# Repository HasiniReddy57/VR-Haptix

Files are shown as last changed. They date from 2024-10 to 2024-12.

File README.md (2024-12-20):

# Haptic Feedback for Stroke Rehabilitation in Virtual Environment
This is a repository to track the progress of our capstone project 'Spinoverse, Haptic Feedback System for enhanced Virtual Reality experience'

# Unity Project Setup Guide

Access the Unity project and follow the setup instructions using the link below:

- **Unity Project Repository**: [VR-Haptix-Environment](https://github.com/HasiniReddy57/VR-Haptix-Environment)

This repository contains the complete Unity project files and a comprehensive setup guide in the README file.

---

### Standalone Unity Environment Setup

The project is designed for standalone environments, ensuring it runs independently with minimal external dependencies. Please refer to the repository's README for detailed instructions.

---

### Credits

VR Environment developed and maintained by [Hasini Patlolla](mailto:hpatloll@uci.edu).

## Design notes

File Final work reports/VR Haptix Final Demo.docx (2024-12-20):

Haptic feedback for stroke rehabilitation in virtual environment

Final Prototype Link:

https://www.youtube.com/watch?v=wLWnkHBS-OE

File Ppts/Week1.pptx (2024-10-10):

## Team Haptix 2.0 Capstone Project Update

## Application Update

Haptix for Physiotherapy/Pain relief
Existing Application
TENS - https://uihc.org/health-topics/transcutaneous-electrical-nerve-stimulator-tens

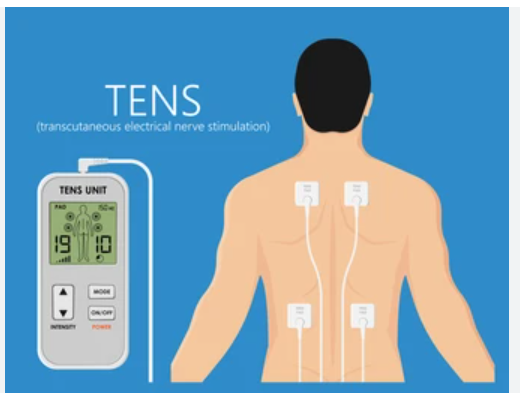
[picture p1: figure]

## System Design

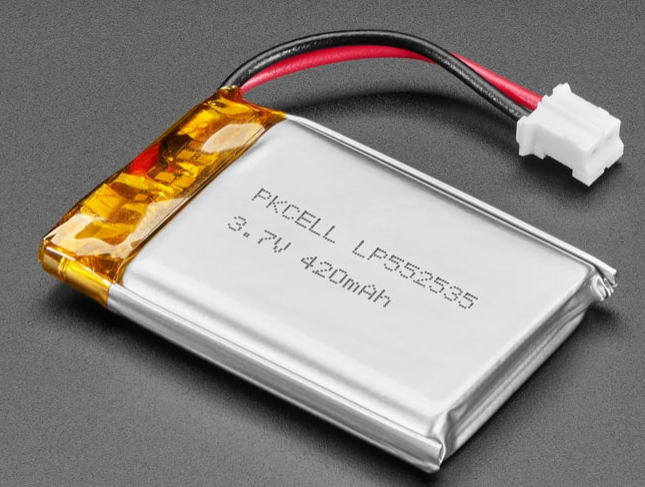
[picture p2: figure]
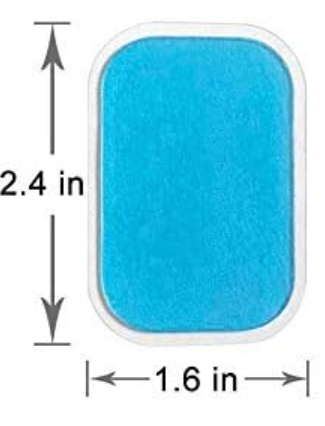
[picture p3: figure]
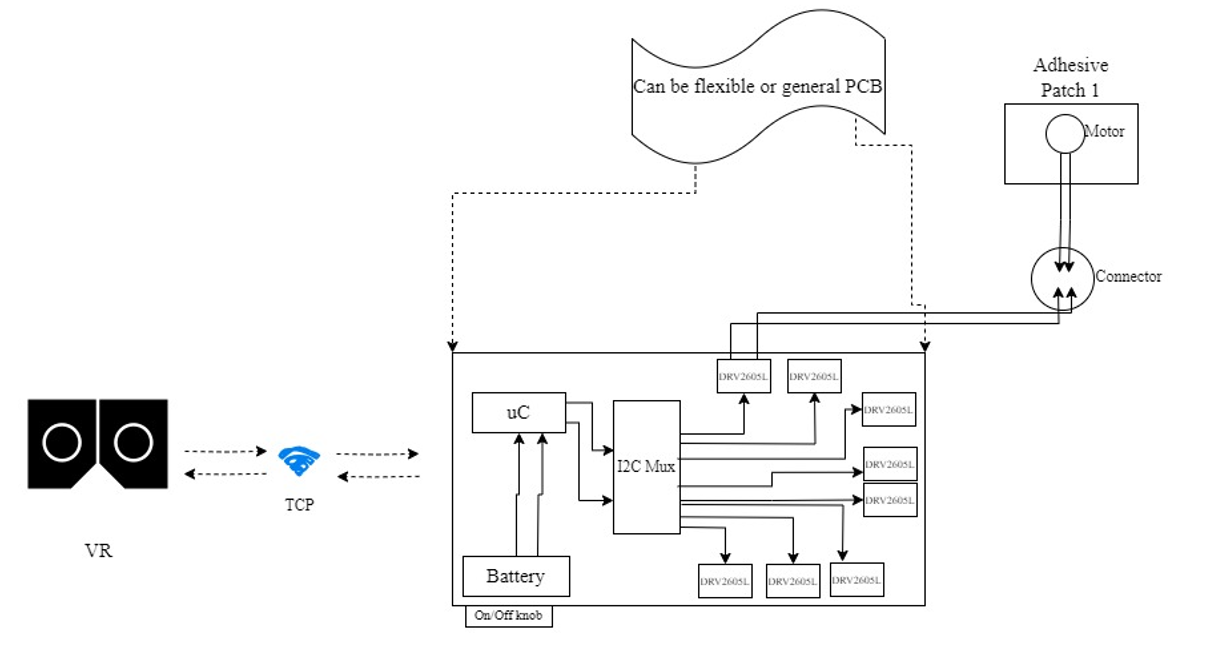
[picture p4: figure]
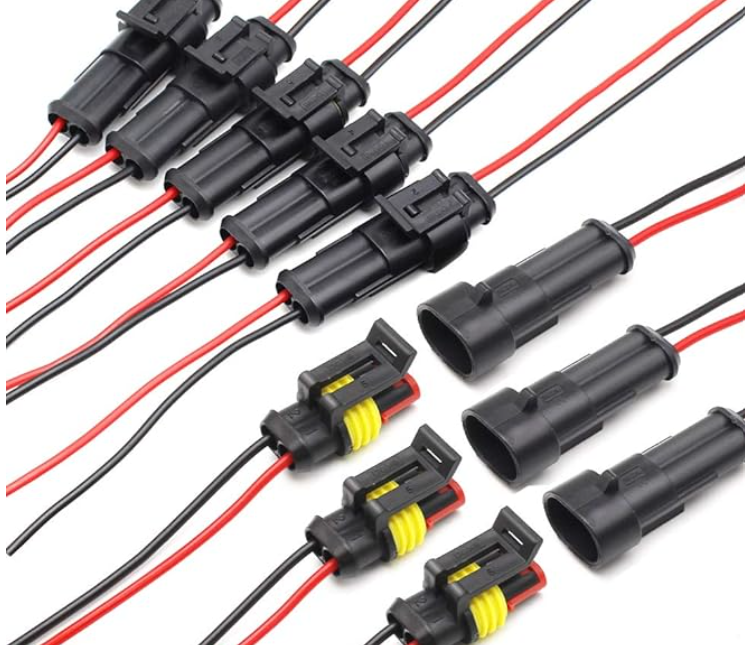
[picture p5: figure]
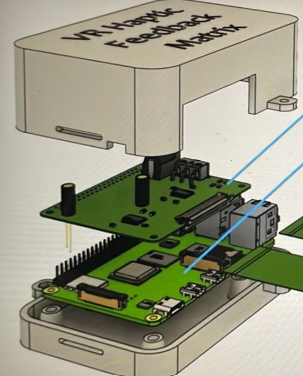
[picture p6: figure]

## Components & Communication

Components
1. DRV2605L
2. Actuator – Tested ERM
3. I2C mux – TCA9548A
4. Controller – ESP32
5. Battery - LiPo
6. Power knob
7. Adhesive patch
8. Connectors
9. VR
Communication
1. I2C
2. TCP

## Voltage, Current, Power requirements

- ERM motor:
- Voltage supply – 2 to 5v
- Current drawn by the motor – 40-80mAmp
- Power – 80-400mW
- ESP32
- Voltage supply – 2 to 5v
- Current drawn by the ESP32 – 80-130mA (without Wifi)
Start up no WiFi 40-45mA, Flash Mode 20-25mA, With WiFi 120-125mA
- Power - 481mW (with Wifi)
- DRV2605L
- Voltage supply – 2 to 5.2v
- Current drawn by the DRV2605L – 10mA to 30mA
- Power - 2.2mW

## Contd…

- TCA9548A
- Voltage supply –1.65V to 5.5V
- Current drawn by the motor – 3μA (inactive) to 600μA (active)
- Power - 15μW to 3mW

## Motor types – ERM, LRA, FEA

## PCB designing

- Followed tutorials on schematic and PCB layout. Need support with routing and further steps.

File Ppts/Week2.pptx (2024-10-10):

## Team Haptix 2.0 Capstone Project Update

## Driver updates

- DRV8833
- DRV2603
- But not for Haptic applications. Supports servo motors.
- DRV2605 & DRV2605L – Haptic drivers with ERM motors

## Power calculations

Tested with 3.3v, 170mAh battery.
Initial battery - 3.869v (actually 4.2v according to datasheet)

- Same Battery connected to ESP32 and other circuit
- Battery voltage – 3.7v
- Run time – 1hr
- When voltage drops to 3.57v, ESP32 went to sleep mode.
- Entire circuit draws 0.169Amps ~ 170mA
- Separate Battery connected to ESP32 and Other circuit
- Battery voltage – 3.81v
- Run time – 1hr 20 mins
- The circuit was working till 3.3v battery but below 3.5v, some On-board LEDs of driver are fluctuating. Not sure if its because of loose connections on bread board.

## PCB Layout

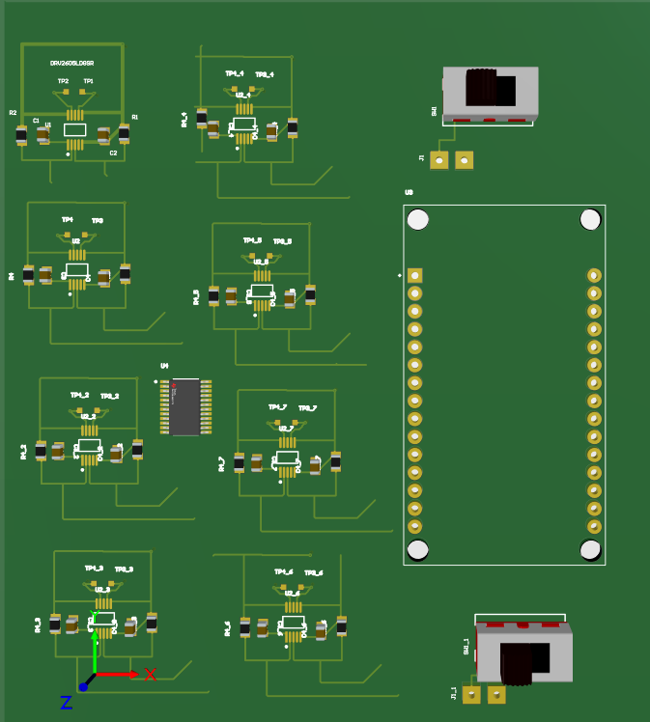
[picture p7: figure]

Rigid PCB - 10x8 Cm

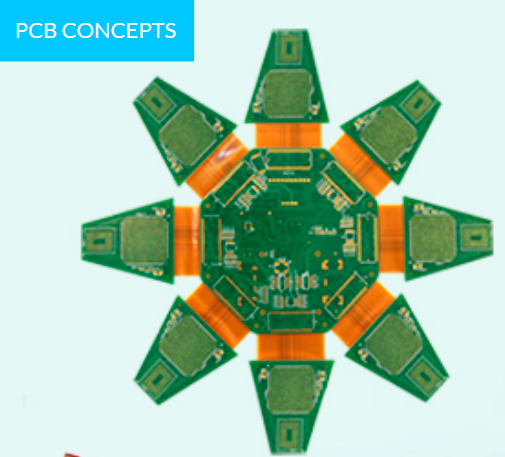
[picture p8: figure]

Flex Rigid PCB

## Software Flow

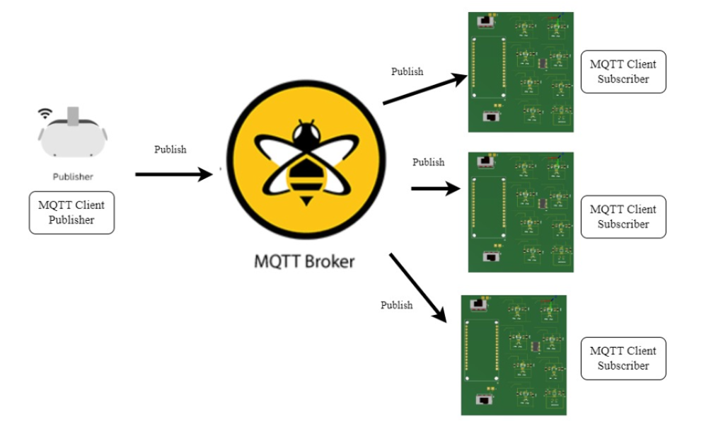
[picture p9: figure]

## Fall Implementation

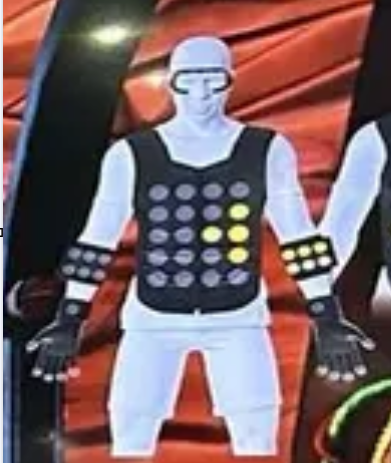
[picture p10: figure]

VR application with a virtual environment room that has some objects like desk, pen, book.
When any object is touched in VR environment, person can feel the touch.
Properties:
Different Intensities different vibrations.
Ripple effect in VR when any object is touched.

Band with Haptic actuators

Haptic Glove

## BT update

nRF52840 SoC

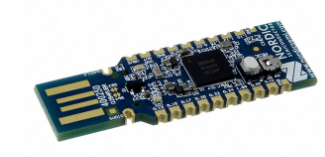
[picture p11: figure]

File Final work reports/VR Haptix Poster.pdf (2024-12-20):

# Haptic Feedback for Stroke Rehabilitation in Virtual Environment

Akshatha Vallampati (avallamp@uci.edu), Swathi Shashidhar (shashidh@uci.edu), Hasini Patlolla (hpatloll@uci.edu) Professor Camilo Velez Cuervo, Professor Rainer Doemer Professional Master of Embedded and Cyber-physical Systems Program, University of California, Irvine

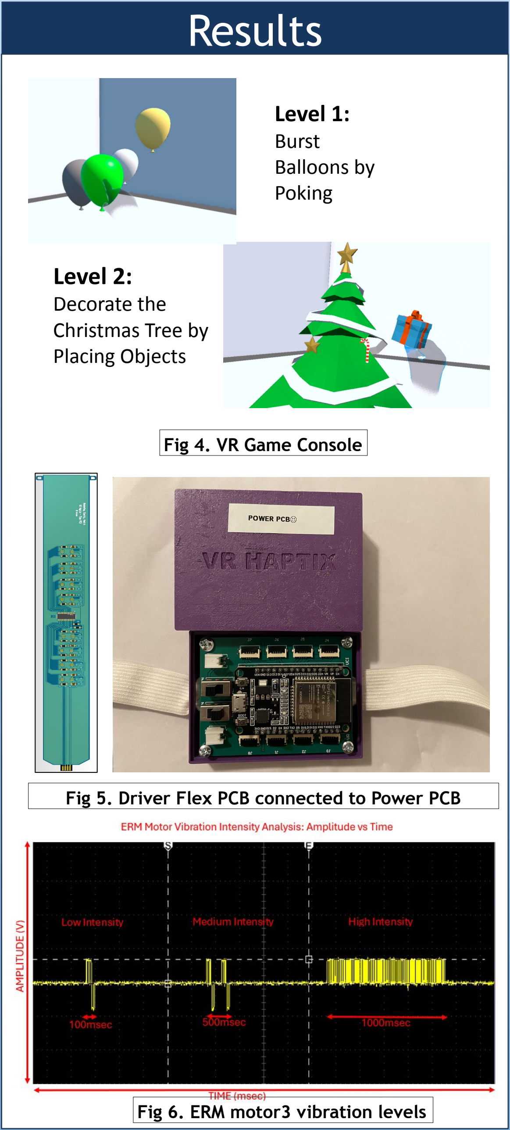
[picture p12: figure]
Fig 4. VR Game Console; Fig 6. ERM motor3 vibration levels; Level 1: Burst Balloons by Poking; Level 2: Decorate the Christmas Tree by Placing Objects

Abstract | System Design & Flow | Results

# Acknowledgements

### www.mecps.uci.edu

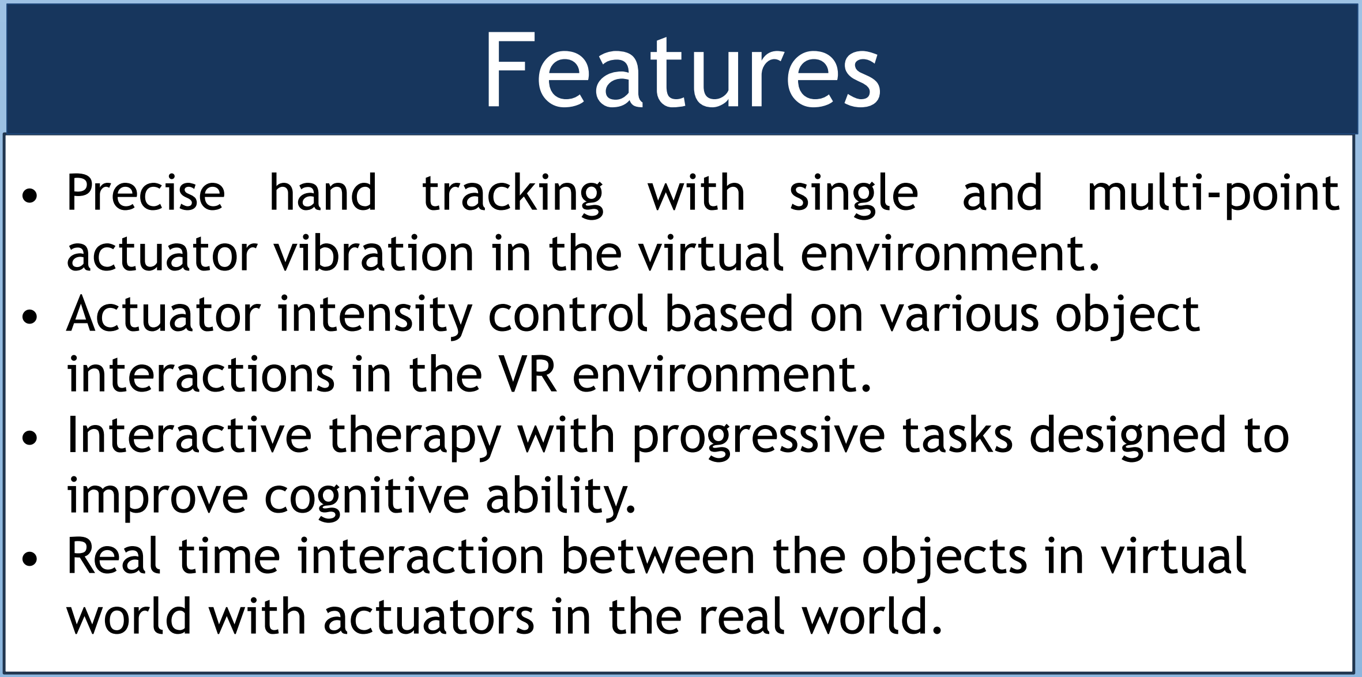
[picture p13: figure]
interactions in the VR environment.; improve cognitive ability.; world with actuators in the real world.; Features

- Precise hand tracking with single and multi-point actuator vibration in the virtual environment.
- Actuator intensity control based on various object
- Interactive therapy with progressive tasks designed to
- Real time interaction between the objects in virtual

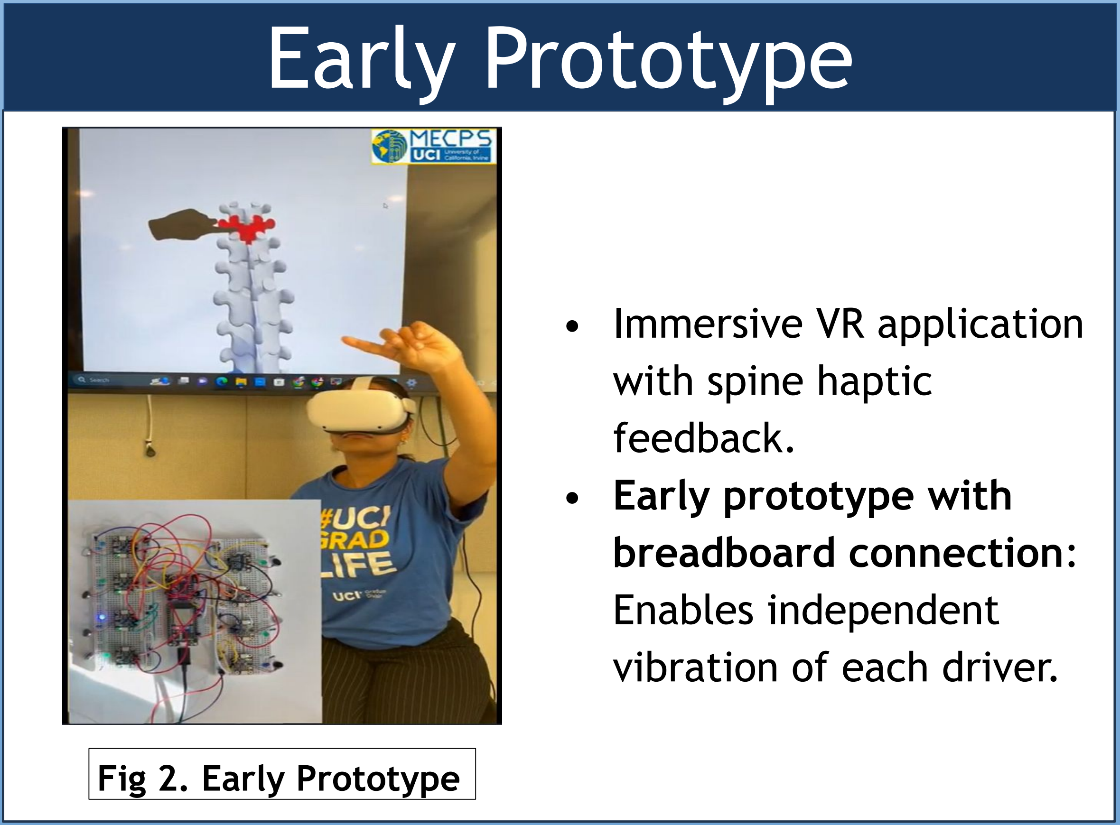
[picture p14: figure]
• Immersive VR application with spine haptic feedback. • Early prototype with breadboard connection: Enables independent vibration of each driver.; Fig 2. Early Prototype

Early Prototype | • | VR Interaction: User hand-tracking in the VR environment maps object interactions to
| | specific actuator coordinates, sending data to ESP32 through TCP communication.
- VR-to-Hardware Communication: The actuator controller processes coordinate and intensity
| | data to determine which ERM motors to activate with their vibration strength.
- Hardware Feedback: Drivers activate ERM motors, delivering precise real-time haptic
| | feedback based on mapped intensity patterns.

# Future Scope

- Single chip integration for multiple actuators.
- Battery optimization for long run.
- Bluetooth integration for Internet-free communication.
- Cloud-based game performance analysis for medical feedback.
- Multi-user connectivity for collaborative virtual environment.

### Connect with us

Fig 3. System Design

Fig 5. Driver Flex PCB connected to Power PCB

- The virtual environment is developed using Unity3D and XR Interaction Toolkit with precise joint tracking using XR Hands package.
- Actuator controller consists of
(a) ESP32 microcontroller, programmed using Arduino IDE
(b) 3.7V, 450mAh LiPo battery that powers the microcontroller for approximately 2.5 hours,
(c) 3.7V, 4000mAh LiPo battery supports the entire system of eight Flex PCBs for up to 2 hours when all motors are active.
- Each of eight Flex PCBs house 8 DRV2605L haptic drivers and 8 ERM motors (total of 64 motors), delivering realistic touch sensations with adjustable intensities.

We extend our sincere gratitude to Meta for funding our project. Special thanks to Mahtab and Shingirirai for their invaluable guidance in PCB design. We also express our gratitude to Professor Doemer for his continuous support and guidance.

Fig 1. Final Prototype

This project combines Virtual Reality (VR) applications with haptic feedback systems to enhance stroke rehabilitation through interactive therapy. Using the Meta Quest 2 VR headset, patients engage in games designed to simulate real-life exercises using hand glove with varying difficulty levels. The system employs an ESP32 microcontroller connected to eight Flex PCBs, each embedded with DRV2605L haptic drivers and ERM motors. These components deliver precise vibration feedback at different intensities (low, medium, high), synchronized with in-game activities.

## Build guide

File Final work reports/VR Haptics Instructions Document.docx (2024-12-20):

Haptic Feedback for Stroke Rehabilitation in Virtual Environment

Instruction Document

Hardware Setup and PCB design – Akshatha (avallamp@uci.edu)

Communication setup and code – Swathi (shashidh@uci.edu)

VR Game Design – Hasini (hpatloll@uci.edu)

MECPS’23-24 students

Hardware Setup:

All components are placed in the box which has Haptix 2.0 (below picture) sticker on it.

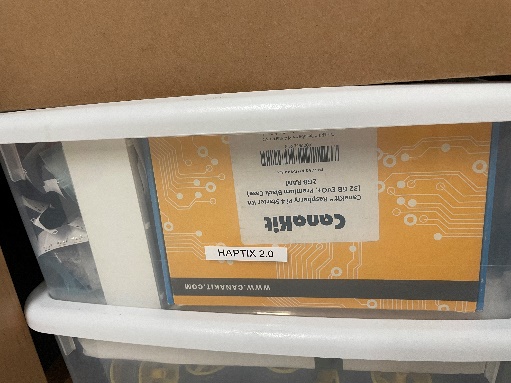
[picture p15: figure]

Prototype picture:

The prototype of this project contains a Haptic glove with Power PCB attached as shown in the below image. It has Flex PCBs (Not working as there’s a fault in the PCB design) attached at the fingers of the glove. Power PCB will have ESP32 microcontroller, 2 LiPo batteries (450mAh already placed in the Power PCB case but not connected), SPDT switch, flex PCB connector (Bottom pin configuration).

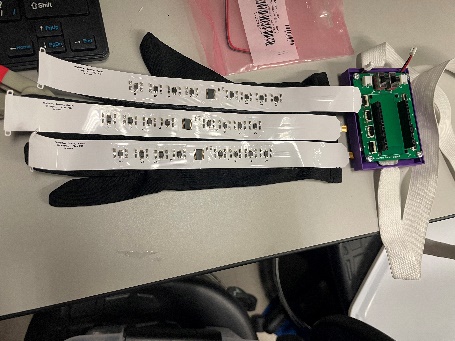
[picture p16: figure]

Power PCB components:

1. ESP32 Wroom 32 controller
2. 2 SPDT switches
3. 2 LiPo batteries
4. 8 Flex connectors

Power PCB Altium design files are attached in GitHub. (Please contact Akshatha for any doubts).

We have used Altium for PCB designing, JLCPCB for fabrication.

Flex PCB components:

1. TCA9548A (I2C mux)
2. DRV2605L
3. ERM motor
4. Resistors, capacitors

Flex PCB Altium design files are attached in GitHub. (Please contact Swathi for any doubts).

Flex PCB already present in the kit are not working because, there are vias (connects tip and bottom layer by drilling) in the PCB design which are not drilled making no connection between top and bottom layer. Tried scratching the top and bottom layer to expose copper, made a hole and soldered a wire, but since the components are nearby, they are coming out of their placement. Better to go with a new flex pcb but with drills.

The kit has ERM motors close to 50 in number. It is placed in a black Adafruit box.

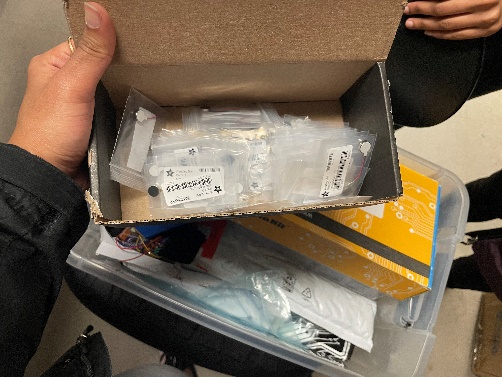
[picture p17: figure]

This below yellow color kit has drivers, flex connectors (both top and bottom configuration)

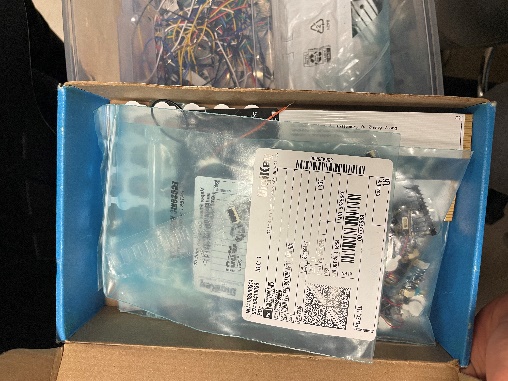
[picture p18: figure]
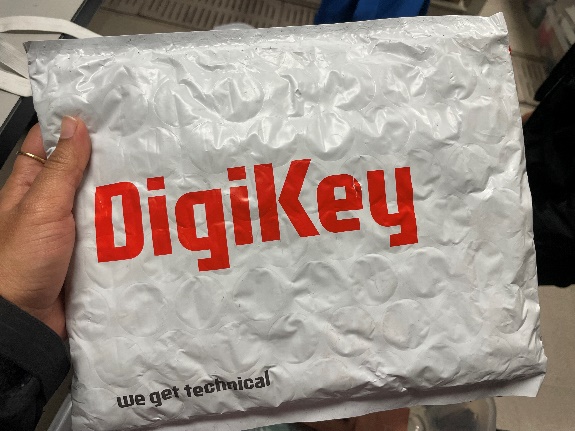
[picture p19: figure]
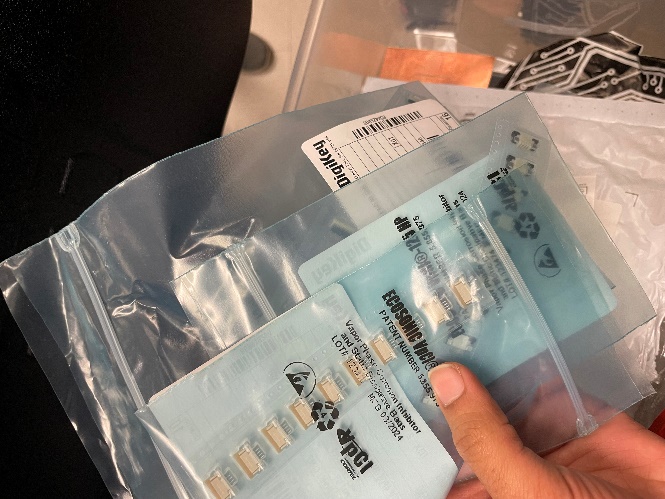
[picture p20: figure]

The below JLCPCB box has batteries, battery connectors, unsoldered power PCBs, LiPo battery charger, switches.

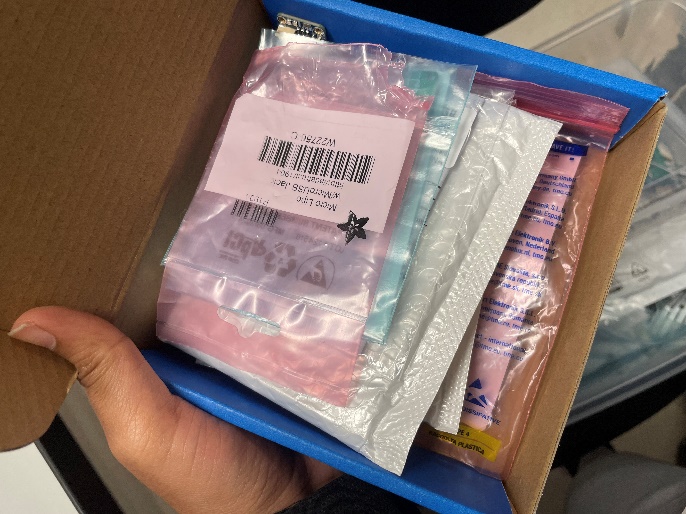
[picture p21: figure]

Apart from this, the kit has Raspberry pi kit, jumper wires, bread boards, LEDs, resistors that were used to make the bread board circuit. Below are the list.

Raspberry pi kit
Power PCB | 3
Glove setup(Power PCB with battery and SPDT)
ESP32
LIPO battery conector
Switch
I2c mux(TCA9548A) | 2
Jumper connectors | In a box
LiPo battery (4000mAh) | 2
Breaad boards | 3
FPC connector | 3 reels
DRV2605L | 15

Hardware Connection Diagram:

References:

1. Lipo Battery Safety Warning (https://power.tenergy.com/lipo-safety-warnings/)
2. ESP32 Wroom 32 Datasheet (https://www.espressif.com/sites/default/files/documentation/esp32-wroom-32_datasheet_en.pdf)
3. DRV2605L datasheet (https://www.ti.com/lit/ds/symlink/drv2605l.pdf)
4. I2C mux datasheet (https://www.ti.com/lit/ds/symlink/tca9548a.pdf)
5. ERM motor Datasheet (https://cdn-shop.adafruit.com/product-files/1201/P1012_datasheet.pdf)

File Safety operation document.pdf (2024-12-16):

SOP for Haptic Feedback for Stroke Rehabilitation in Virtual Environments

Purpose

This SOP provides step-by-step instructions for assembling and operating a haptic feedback system integrated with a Meta Quest2 VR application. The system is designed to aid stroke patients through immersive therapy, enhancing physical rehabilitation by combining VR exercises with precise haptic feedback. This document ensures consistent procedures, maximizes safety, and helps mitigate potential risks associated with handling batteries and haptic motor components.

Context

This procedure is designed to guide stroke patients and their assisting healthcare providers, such as nurses or therapists, in using the VR Haptix system safely and effectively. By following these instructions, patients can engage in immersive therapy that enhances their recovery experience, while healthcare providers can ensure consistent operation and optimal performance of the system.

Definitions

- Haptic Feedback: Technology that simulates the sense of touch through vibrations or motions.
- ERM Motor: Eccentric Rotating Mass motor, used for generating vibration.
- DRV2605L: A haptic driver IC used to control vibration intensity and patterns.
- TCA9548A: An I2C mux for connecting multiple drivers and motors.
- LiPo Battery: A Lithium Polymer battery used as the primary power source for the system.

Tools and Equipment

- Hardware Components:
- ESP32 Microcontroller
- Eight Flex PCBs with TCA9548A mux, DRV2605L drivers and 64 ERM motors
- 3.7V, 450mAh LiPo battery (microcontroller power)
- 3.7V, 4000mAh LiPo battery (Flex PCB power)
- Battery level Indicator
- Meta Quest2 VR headset
- SPDT swicthes
- Software Requirements:
- VR Haptix application

- Software for TCP, I2C communication setup

How to Assemble and Operate the System

### 1. Battery Management

1.1 Check the charge level of LiPo batteries using a multimeter. Ensure they are at a safe charge level (between 20% - 80% for storage, fully charged for testing).
1.2 If charging is needed, place batteries in a fireproof bag and connect them to a compatible charger. Do not leave unattended during charging.
1.3 Store batteries in a fireproof bag when not in use.
1.4 Dispose of damaged batteries following proper e-waste guidelines.

### 2. Hardware Assembly

2.1 Connect the ESP32 microcontroller which is the Power PCB to the Flex PCBs using FPC connectors.
2.2 Power the system:
- Use the 450mAh LiPo battery for the microcontroller.
- Use the 4000mAh LiPo battery for the Flex PCBs.
2.3 Connect the DRV2605L to the microcontroller using I2C. Ensure proper connections (SDA, SCL, VCC, GND).
2.4 Load the appropriate haptic feedback libraries into the Arduino IDE.
2.5 Upload a test sketch to verify communication between the microcontroller and DRV2605L. 2.6 Use predefined vibration profiles to test each driver, ensuring accurate response.

### 3. Software Setup

3.1 Install the VR Haptix application on the Meta Quest2 headset.
3.2 Establish TCP communication between the headset and the ESP32 microcontroller. Begin by running the controller code to initialize the system. Once the controller is active, launch the Unity application, which will automatically establish a connection to the WiFi network.
3.3 Ensure that the same code has I2C communication setup with mux and drivers as well.

### 4. Testing

4.1 Start the VR Haptix application and calibrate the intensity levels.
4.2 Test individual motor vibrations for accuracy and ensure simultaneous actuation.
4.3 Validate therapy levels (easy, medium, hard) with corresponding haptic feedback intensity. 4.4 Perform a basic functionality test with a safe, low-intensity vibration pattern to ensure proper behavior.
4.5 Gradually increase intensity and test each functionality (including waveform selection) to validate performance.

### 5. Operational Guidelines

5.1 Ensure the batteries are fully charged before use. There is a battery indicator used. If it turns red, then the batteries has to charged.
5.2 If an ERM motor overheats, stop testing immediately, allow it to cool down, and inspect for damage.
5.3 Follow safety protocols for handling LiPo batteries to avoid overheating or damage.
5.4 Monitor the system for consistent feedback during therapy sessions.

### 6. Post-Session Maintenance

6.1 Disconnect all power sources after each session.
6.2 Inspect hardware for wear or damage.
6.3 Update software to the latest version, if available.

### 7. Documentation

7.1 Record battery usage, including charge cycles, voltage before and after each test, and any abnormalities.
7.2 Maintain logs for vibration intensity tests, including any changes to default parameters. 7.3 Keep track of component wear and tear, especially for ERM motors and battery health.

References

- Meta Quest2 User Guide (https://www.meta.com/help/quest/articles/getting-started/getting-started-with-quest-2/)
- Lipo Battery Safety Warning (https://power.tenergy.com/lipo-safety-warnings/)
- ESP32 Wroom 32 Datasheet (https://www.espressif.com/sites/default/files/documentation/esp32-wroom-32_datasheet_en.pdf)
- DRV2605L datasheet (https://www.ti.com/lit/ds/symlink/drv2605l.pdf)
- I2C mux datasheet (https://www.ti.com/lit/ds/symlink/tca9548a.pdf)
- ERM motor Datasheet (https://cdn-shop.adafruit.com/product-files/1201/P1012_datasheet.pdf)

Contact:

For more details or information, please contact

Akshatha Vallampati – avallamp@uci.edu

Swathi Shahidhar - shashidh@uci.edu

Hasini Patlolla - hpatloll@uci.edu

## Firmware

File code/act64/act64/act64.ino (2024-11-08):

/* below I2C channels verified - on 10/21/2024
21,22 - Ch1 - Working
19,23 - Ch2 - Working
18,5 - Ch3 - Working
17,16 - Ch4 - Working
15,14 - Ch5 - Working
25,13 - Ch6 - Working
33,32 - Ch7 - Working
27,26 - Ch8 - Working
*/
#include <Wire.h>
#include <Adafruit_DRV2605.h>

// Define the I2C addresses for each multiplexer
#define I2C_MUX_ADDR_1 0x70  // I2C address for Mux1
#define I2C_MUX_ADDR_2 0x71  // I2C address for Mux2
#define I2C_MUX_ADDR_3 0x72  // I2C address for Mux3
#define I2C_MUX_ADDR_4 0x73  // I2C address for Mux4
#define I2C_MUX_ADDR_5 0x74  // I2C address for Mux5
#define I2C_MUX_ADDR_6 0x75  // I2C address for Mux6
#define I2C_MUX_ADDR_7 0x76  // I2C address for Mux7
#define I2C_MUX_ADDR_8 0x77  // I2C address for Mux8

// Declare DRV2605 objects
Adafruit_DRV2605 drv1, drv2, drv3, drv4, drv5, drv6, drv7, drv8;
Adafruit_DRV2605 drv9, drv10, drv11, drv12, drv13, drv14, drv15, drv16;
// Add more drv objects for the remaining drivers if needed

// Define I2C pins for each mux
#define SDA_PIN_1 5         // I2C SDA pin for Mux1
#define SCL_PIN_1 18         // I2C SCL pin for Mux1

#define SDA_PIN_2 21         // I2C SDA pin for Mux2
#define SCL_PIN_2 19         // I2C SCL pin for Mux2

#define SDA_PIN_3 22         // I2C SDA pin for Mux3
#define SCL_PIN_3 23          // I2C SCL pin for Mux3

#define SDA_PIN_4 33         // I2C SDA pin for Mux4
#define SCL_PIN_4 32         // I2C SCL pin for Mux4

#define SDA_PIN_5 25         // I2C SDA pin for Mux5
#define SCL_PIN_5 26         // I2C SCL pin for Mux5

#define SDA_PIN_6 14         // I2C SDA pin for Mux6
#define SCL_PIN_6 27         // I2C SCL pin for Mux6

#define SDA_PIN_7 13         // I2C SDA pin for Mux7
#define SCL_PIN_7 17         // I2C SCL pin for Mux7

#define SDA_PIN_8 15         // I2C SDA pin for Mux8
#define SCL_PIN_8 16         // I2C SCL pin for Mux8

// Create separate TwoWire instances for each I2C bus
TwoWire wire1 = TwoWire(0);
TwoWire wire2 = TwoWire(1);
TwoWire wire3 = TwoWire(2);
TwoWire wire4 = TwoWire(3);
TwoWire wire5 = TwoWire(4);
TwoWire wire6 = TwoWire(5);
TwoWire wire7 = TwoWire(6);
TwoWire wire8 = TwoWire(7);

// Function to select the mux channel
void selectMuxChannel(TwoWire &wire, uint8_t muxAddr, uint8_t channel) {
  if (channel > 7) return;  // Check if the channel is valid
  wire.beginTransmission(muxAddr);
  wire.write(1 << channel);  // Select the channel
  wire.endTransmission();
}

void setup() {
  Serial.begin(115200);
  delay(10);

  // Initialize the I2C buses
  wire1.begin(SDA_PIN_1, SCL_PIN_1);
  wire2.begin(SDA_PIN_2, SCL_PIN_2);
  wire3.begin(SDA_PIN_3, SCL_PIN_3);
  wire4.begin(SDA_PIN_4, SCL_PIN_4);
  wire5.begin(SDA_PIN_5, SCL_PIN_5);
  wire6.begin(SDA_PIN_6, SCL_PIN_6);
  wire7.begin(SDA_PIN_7, SCL_PIN_7);
  wire8.begin(SDA_PIN_8, SCL_PIN_8);

  // Initialize DRV2605s on each multiplexer
  Adafruit_DRV2605* drvArray[] = {&drv1, &drv2, &drv3, &drv4, &drv5, &drv6, &drv7, &drv8, &drv9, &drv10, &drv11, &drv12, &drv13, &drv14, &drv15, &drv16};

  // Loop through all 8 I2C buses and initialize DRV2605 drivers
  for (uint8_t i = 0; i < 8; i++) {
    selectMuxChannel(wire1, I2C_MUX_ADDR_1, i);
    if (!drvArray[i]->begin(&wire1)) {
      Serial.print("Failed to find DRV2605 on Mux1 channel ");
      Serial.println(i);
      while (1);
    }
    drvArray[i]->selectLibrary(1);
    drvArray[i]->setMode(DRV2605_MODE_INTTRIG);
  }

  // Repeat this process for all other muxes (you can copy the same logic for Mux2 to Mux8)
  // Example for Mux2:
  for (uint8_t i = 0; i < 8; i++) {
    selectMuxChannel(wire2, I2C_MUX_ADDR_2, i);
    if (!drvArray[i]->begin(&wire2)) {
      Serial.print("Failed to find DRV2605 on Mux2 channel ");
      Serial.println(i);
      while (1);
    }
    drvArray[i]->selectLibrary(1);
    drvArray[i]->setMode(DRV2605_MODE_INTTRIG);
  }
}

void loop() {
  // Activate all drivers simultaneously
  for (uint8_t i = 0; i < 8; i++) {
    selectMuxChannel(wire1, I2C_MUX_ADDR_1, i);
    drv1.setWaveform(0, 15);  // Play effect 15
    drv1.go();
    // Add code for other drivers
  }

  delay(1000);  // Delay between activations
}

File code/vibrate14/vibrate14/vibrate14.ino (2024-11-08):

//vibrate all 14 same time
//working- tested on 10/15/2024
#include <Wire.h>
#include <Adafruit_DRV2605.h>

// Define I2C multiplexers' addresses
#define I2C_MUX1_ADDR 0x70  // I2C address for mux1
//#define I2C_MUX2_ADDR 0x77  // I2C address for mux2

Adafruit_DRV2605 drv1, drv2, drv3, drv4, drv5, drv6, drv7, drv8; // Motors on mux1
//Adafruit_DRV2605 drv9, drv10, drv11, drv12, drv13, drv14; // Motors on mux2

#define SDA_PIN1 15       // Custom I2C SDA pin for Mux1
#define SCL_PIN1 16        // Custom I2C SCL pin for Mux1
//#define SDA_PIN2 19         // Custom I2C SDA pin for Mux2
//#define SCL_PIN2 21         // Custom I2C SCL pin for Mux2

#define DRV1_CHANNEL 0     // Channel for drv1
#define DRV2_CHANNEL 1     // Channel for drv2
#define DRV3_CHANNEL 2     // Channel for drv3
#define DRV4_CHANNEL 3     // Channel for drv4
#define DRV5_CHANNEL 4     // Channel for drv5
#define DRV6_CHANNEL 5     // Channel for drv6
#define DRV7_CHANNEL 6     // Channel for drv7
#define DRV8_CHANNEL 7     // Channel for drv8
/*
#define DRV9_CHANNEL 0     // Channel for drv9 on mux2
#define DRV10_CHANNEL 1    // Channel for drv10 on mux2
#define DRV11_CHANNEL 2    // Channel for drv11 on mux2
#define DRV12_CHANNEL 3    // Channel for drv12 on mux2
#define DRV13_CHANNEL 4    // Channel for drv13 on mux2
#define DRV14_CHANNEL 5    // Channel for drv14 on mux2
*/
TwoWire myWire1 = TwoWire(0); // Create a new TwoWire instance for the first I2C bus (Mux1)
TwoWire myWire2 = TwoWire(1); // Create a new TwoWire instance for the second I2C bus

void selectMuxChannel(TwoWire &wire, uint8_t muxAddr, uint8_t channel) {
  if (channel > 7) return;
  wire.beginTransmission(muxAddr);
  wire.write(1 << channel);
  wire.endTransmission();
}


//void resetDevice(Adafruit_DRV2605 &drv) {
//  drv.writeRegister8(0x16, 0x01); // Reset command for DRV2605L
//  delay(10);  // Small delay to allow reset to complete
//}


void setup() {
  Serial.begin(115200);
  delay(10);

  // Initialize I2C buses for the multiplexers
  myWire1.begin(SDA_PIN1, SCL_PIN1);
  //myWire2.begin(SDA_PIN2, SCL_PIN2);

  // Initialize drv1 to drv8 on the first mux
  Adafruit_DRV2605* drvArray1[] = {&drv1, &drv2, &drv3, &drv4, &drv5, &drv6, &drv7, &drv8};
  for (uint8_t i = 0; i < 8; i++) {
    selectMuxChannel(myWire1, I2C_MUX1_ADDR, i);  // Select the channel on mux1
  //  resetDevice(*drvArray1[i]);  // Perform a reset before initialization
  //drvArray1[i]->writeRegister8(DRV2605_REG_MODE, 0x80);
  delay(100);
    if (!drvArray1[i]->begin(&myWire1)) {
      Serial.print("Failed to find DRV2605 on mux1 channel ");
      Serial.println(i);
      while (1); // Stop if a device isn't found
    }
    drvArray1[i]->selectLibrary(1);
    drvArray1[i]->setMode(DRV2605_MODE_INTTRIG);
  }
/*
  // Initialize drv9 to drv14 on the second mux
  Adafruit_DRV2605* drvArray2[] = {&drv9, &drv10, &drv11, &drv12, &drv13, &drv14};
  for (uint8_t i = 0; i < 6; i++) {
    selectMuxChannel(myWire2, I2C_MUX2_ADDR, i);  // Select the channel on mux2
    //resetDevice(*drvArray2[i]);  // Perform a reset before initialization
    writeRegister8(DRV2605_REG_MODE, 0x80);
    if (!drvArray2[i]->begin(&myWire2)) {
      Serial.print("Failed to find DRV2605 on mux2 channel ");
      Serial.println(i);
      while (1); // Stop if a device isn't found
    }
    drvArray2[i]->selectLibrary(1);
    drvArray2[i]->setMode(DRV2605_MODE_INTTRIG);
  }*/
}

void loop() {
  // Activate drv1 to drv8 at the same time
  Adafruit_DRV2605* drvArray1[] = {&drv1, &drv2, &drv3, &drv4, &drv5, &drv6, &drv7, &drv8};
  for (uint8_t i = 0; i < 8; i++) {
    selectMuxChannel(myWire1, I2C_MUX1_ADDR, i);  // Select the corresponding channel
    drvArray1[i]->setWaveform(0, 15);  // Play effect 15
    drvArray1[i]->go();
  }
/*
 // Activate drv9 to drv14 at the same time
  Adafruit_DRV2605* drvArray2[] = {&drv9, &drv10, &drv11, &drv12, &drv13, &drv14};
  for (uint8_t i = 0; i < 6; i++) {
    selectMuxChannel(myWire2, I2C_MUX2_ADDR, i);  // Select the corresponding channel
    drvArray2[i]->setWaveform(0, 15);  // Play effect 15
    drvArray2[i]->go();
  }
*/
  delay(1000);  // Delay for demonstration purposes before looping again
}

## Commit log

2024-10-27 Power PCB files
    [powerPCB.PcbDoc, powerPCB.PcbLib, powerPCB.PrjPcb, powerPCB.SchDoc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]
2024-12-20 Create Project Output for Flex PCB
